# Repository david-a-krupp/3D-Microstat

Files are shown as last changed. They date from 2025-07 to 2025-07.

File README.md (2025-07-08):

# 3D-Microstat
Open-source 3D Clinostat design inspired by iGEM Concordia. This Clinostat was designed by a team of University of Georgia students for the Small Satellite Research Laboratory to support space biology research and microgravity experiments. This final product occupies very little space compared to most other COTS (Commercial-off-the-Shelf) Clinostats, taking up roughly 350 x 300 x 320 mm of space when fully assembled. Build instructions are included below, though the best assembly help will come from viewing the full Microstat assembly (located in CAD files) and viewing the wiring diagram provided.

**Preface -**

This Clinostat build requires a degree of project-specific tailoring. The 140 x 140 mm payload platform is a hard limit for this form factor without increasing the size of the swingarm. The weight restriction varies by geometry and how far from the platform's surface your payload protrudes. The given platform geometry (STL, CAD file) includes M3 fastener holes that can be used for either designing your own mount to add in addition, OR to temporarily secure your payload to the platform. The given Bill of Materials includes all resources used to build the model you see in the CAD model, and pictures/media. I am sure there are cheaper alternatives available from places such as McMaster-Carr that do not leave much excess hardware. Again, this is just what I used to build this at a decent cost. For any recommendations regarding better part selections, please commit an updated file with the updated part description and links so that we can continuously improve this design. Thanks! 

<table>
  <tr>
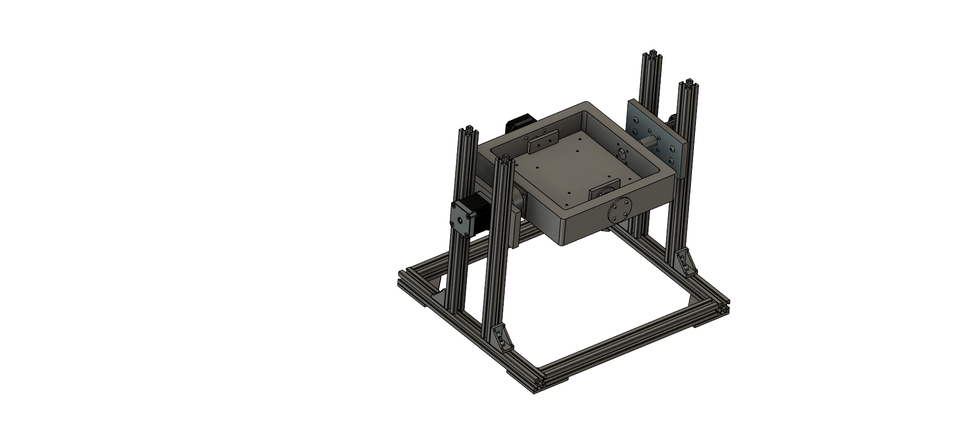
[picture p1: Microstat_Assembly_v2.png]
Microstat CAD Assembly
    <td></td>
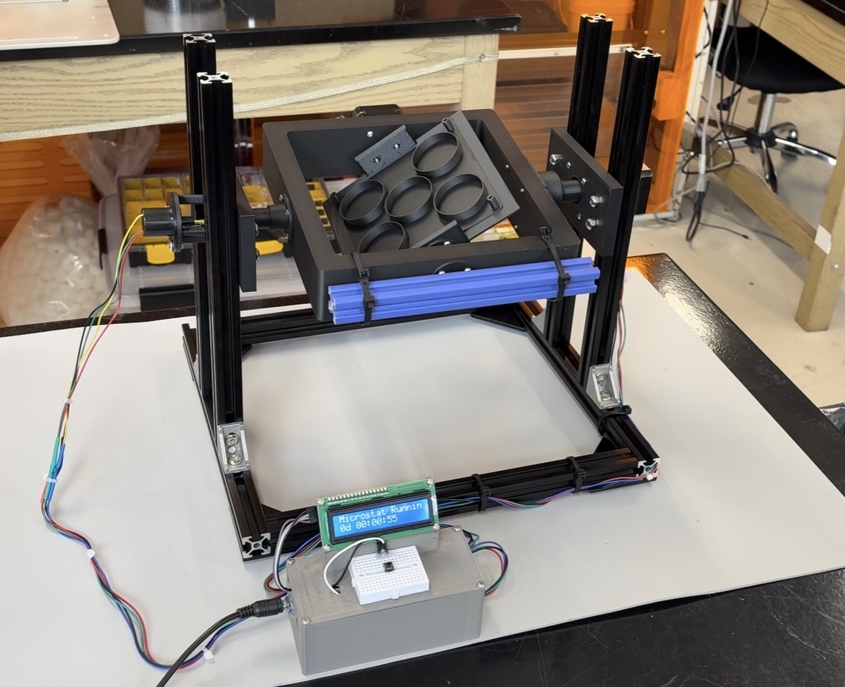
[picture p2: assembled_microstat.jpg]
Assembled Microstat
    <td></td>
  </tr>
</table>

**Build Instructions -** 

Begin by preparing all of the 3D printed parts required for the Microstat. Once the parts are printed, inspect them for any defects or rough edges and carefully remove any excess material or supports. Assemble the main frame by connecting the printed arm, brackets, and base structure as shown in the CAD assembly image. Make sure all moving parts rotate freely and align properly before tightening any fasteners. The 20.5 mm motor should be mounted to the arm before mounting the arm to the frame. Once the 20.5 mm motor is secured, run its 4 wires into the channel in the arm and out the adjacent side. These wires will exit the main assembly through the long rod towards the slip ring mount. 

Next, mount the larger stepper motor to the main axis bracket using the appropriate screws and ensure it is securely fixed in place. Once both motors are mounted, connect the rotating arm to the main axis so that the two axes of rotation are perpendicular, allowing for true 3D rotation. Adjust any extensions or brackets if needed to minimize friction and wobble. Important note: as seen in the provided media, I added balast to the swingarm opposite the side of the 20.5 mm motor to ensure smooth rotation. If you bought the 10pcs aluminum extrusion package from the BoM, I recommend cutting 100 mm off one of the extras and zip tying the 200 mm segment to the swingarm as shown. Otherwise, you may use anything you have that is near the mass of the 20.5 mm motor.

After the mechanical structure is complete, begin wiring the electronics. Connect each stepper motor to its driver module according to the wiring diagram, double-checking the coil pairs to ensure correct rotation. Attach the driver modules to the Arduino Nano, making sure the power and ground connections are secure. Connect the LCD with the I2C backpack to the designated SDA and SCL pins on the Arduino. Install the push button on a separate small breadboard and attach it to the top of the controller case, in front of the LCD. Once the electronics assembly is complete, lower the breadboard with all connections into the case and close it with the lid on top.

Once the wiring is complete, upload the Arduino code provided in this repository to the Nano. Power up the system and test.

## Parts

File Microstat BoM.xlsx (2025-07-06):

Microstat BoM
PRODUCT NAME | Clinostat | INFO |  | #VALUE!
APPROVED BY | David Krupp
DATE OF APPROVAL | 2025-07-01 | White Bold Indicates: Printable Part
ORDER/PART COUNT | 34 | Red Bold Indicates: Part Requiring Order
TOTAL COST | $223.25 | Green Bold Indicates: Ordered Part
PART NUMBER | PART NAME | DESCRIPTION | QUANTITY | UNITS | PART IMAGE | UNIT COST | AMOUNT
1 | Bar Corner Connection (Base) | 4 screwed irregular-pentagon corner connections. TAKES M5 SCREWS (STANDARD/ORDERABLE) [ShortxWxHxThickness] | QUANTITY 1 OF ORDER LINK |  | https://www.amazon.com/Bracket-Anodised-Outside-Aluminum-Extrusion/dp/B07ZQFJ2CK?s=industrial |  | $14.99
2 | Bar 90Deg Connection (Base) | 2 screwed 90Deg connection for upright vertical bars. M5 SCREWS/T-NUTS INCLUDED (STANDARD/ORDERABLE) | QUANTITY 1 OF ORDER LINK |  | https://www.amazon.com/Bracket-Connectors-Aluminum-Extrusion-Accessories/dp/B0B9JVW5X8?s=hi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 |  | $12.99
3 | M3 Fastenings | M3 fasteners for all motor, swivel, blockoff, and non-frame structural componets. | QUANTITY 1 OF ORDER LINK | M3 | https://www.amazon.com/iexcell-Thread-Stainless-Socket-Screws/dp/B07CXKDJ7X?mcid=0fc05dd91ca439b4976eff2272593c81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 |  | $9.96
4 | M5 Fastenings | M5 fasteners needed for frame componets and motor/rod mounting. | QUANTITY 1 OF ORDER LINK | M5 | https://www.amazon.com/Kadrick-Button-Assortment-Stainless-Washers/dp/B0BZ7YZY3D?s=hi |  | $9.99
5 | M5 T-nuts | For assembling the frame. | QUANTITY 1 OF ORDER LINK | M5 | https://www.amazon.com/HELIFOUNER-Pieces-2020-Aluminum-Profile/dp/B0B1LTRYR5?cv_ct_cx=m5%2Bt-nuts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 |  | $5.99
6 | Aluminum Extrusions (300mm) | Diagonally supported long-running base bars (STANDARD/ORDERABLE) [LxWxD] | QUANTITY 2 OF ORDER LINK |  | https://www.amazon.com/Aluminum-Extrusion-European-Standard-7-874inch/dp/B08744RN57?cv_ct_cx=20x20%2BAluminum%2BExtrusion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 |  | $35.98
7 | TMC2209 UART Stepper Motor Drivers | Nema 17 motors require these instead of the DRV8825. The 48mm motor can require up to 2 amps. These supply up to 2.8 amps. | QUANTITY 1 OF ORDER LINK |  | https://www.amazon.com/dp/B08SMDY3SQ?ref=ppx_yo2ov_dt_b_fed_asin_title&th=1 |  | $13.99
8 | 48 mm Nema 17 Stepper Motor | High Torque Motor for main swingarm | QUANTITY 1 OF ORDER LINK |  | https://www.amazon.com/dp/B00PNEQKC0?ref=ppx_yo2ov_dt_b_fed_asin_title |  | $13.99
9 | 20.5 mm Nema 17 Stepper Motor | Small Stepper for inner arm | QUANTITY 1 OF ORDER LINK |  | https://www.amazon.com/dp/B0D22GZFPC?ref=ppx_yo2ov_dt_b_fed_asin_title&th=1 |  | $9.49
10 | Slip Ring | (22 mm, 4-channel, 5 amp maximum) | QUANTITY 1 OF ORDER LINK |  | https://www.aliexpress.us/item/2251832799374262.html |  | $13.49
11 | Arduino Nano Microcontroller | Attached link comes with 3 controllers, only one is needed, no single boards avaliable for cheaper. | QUANTITY 1 OF ORDER LINK |  | https://www.amazon.com/LAFVIN-Board-ATmega328P-Micro-Controller-Arduino/dp/B07G99NNXL?s=industrial |  | $15.99
12 | Breadboards (Mini, 6pcs) | Comes with 6 small breadboards for the controller case. This can be substituted for one larger breadboard for simplicity ***control case edit required***. | QUANTITY 1 OF ORDER LINK |  | https://www.amazon.com/WWZMDiB-SYB-170-Breadboard-Colorful-Multicolored/dp/B0B827VM95?s=industrial |  | $5.99
13 | 1602 LCD Screen (3pcs) | With I2C backpack for wiring simplicity. Comes with 3 pieces. | QUANTITY 1 OF ORDER LINK |  | https://www.amazon.com/Hosyond-Display-Module-Arduino-Raspberry/dp/B0BWTFN9WF?s=industrial |  | $12.99
14 | Jumper Wires | For assembling the Clinostat controller. | QUANTITY 1 OF ORDER LINK |  | https://www.amazon.com/EDGELEC-Breadboard-Optional-Assorted-Multicolored/dp/B07GD2BWPY?s=industrial&sp_csd=d2lkZ2V0TmFtZT1zcF9hdGY |  | $6.98
15 | Terminal Block Connectors | For controller, connects both power supply and the steppers to the breadboards. | QUANTITY 1 OF ORDER LINK |  | https://www.amazon.com/dp/B07H5G7GC6?ref=ppx_yo2ov_dt_b_fed_asin_title |  | $8.99
16 | Female DC Barrel Plug Connector | 16 AWG power supply cable, needs to be attached to a male cable 12V 5amp power supply. | QUANTITY 1 OF ORDER LINK |  | https://www.amazon.com/Pigtails-Connector-Adapter-Security-Surveillance/dp/B0C5DWVGJ8 |  | $9.99
17 | 12V 5A Power Supply | DC Output Jack | QUANTITY 1 OF ORDER LINK |  | https://www.amazon.com/dp/B0CW2PJQLJ?ref=ppx_yo2ov_dt_b_fed_asin_title |  | $9.98
18 | Heat Shrink | For splicing the 20.5 mm Stepper Motor wires with the slip ring interface. Will need to be done on both sides of the slip ring for proper cable length. | QUANTITY 1 OF ORDER LINK |  | https://www.amazon.com/108PCS-Heat-Shrink-Tubing-Kit/dp/B0DRKLWLY5 |  | $4.99
19 | Pushbutton | Push button for Arduino/breadboard. 20 buttons included, only one needed. | QUANTITY 1 OF ORDER LINK |  | https://www.amazon.com/DIYables-Button-Arduino-ESP8266-Raspberry/dp/B0BXKN4TY6?s=electronics |  | $6.49
20 | Outer Arm | PLA, ASA, or ABS. 20% Infill, 0.2 mm or lower layer height recommended. No Supports. | QUANTITY 1 | 200 x 200 x 45 mm
21 | Payload Platform | PLA, ASA, or ABS. 20% Infill, 0.2 mm or lower layer height recommended. Supports needed. | QUANTITY 1 | 140 x 140 x 40 mm
22 | Small Motor Shaft Extension | PLA, ASA, or ABS. 20% Infill, 0.2 mm or lower layer height recommended. | QUANTITY 1 | 35 x 35 x 20 mm
23 | Large Motor Shaft Extension | PLA, ASA, or ABS. 20% Infill, 0.2 mm or lower layer height recommended. | QUANTITY 1 | 45 x 45 x 50 mm
24 | 20 mm Rod Swivel | PLA, ASA, or ABS. 20% Infill, 0.2 mm or lower layer height recommended. | QUANTITY 2 | ⌀40 mm, 15 mm
25 | Slip Ring Mount | PLA, ASA, or ABS. 20% Infill, 0.2 mm or lower layer height recommended. Supports needed. | QUANTITY 1 | ⌀44 mm, 35 mm
26 | Short Rod Blockoff | PLA, ASA, or ABS. 20% Infill, 0.2 mm or lower layer height recommended. | QUANTITY 1 | ⌀40 mm, 2 mm
27 | Short Rod | PLA, ASA, or ABS. 20% Infill, 0.2 mm or lower layer height recommended. | QUANTITY 1 | ⌀15.5 mm, 27 mm
28 | Long Rod | PLA, ASA, or ABS. 20% Infill, 0.2 mm or lower layer height recommended. | QUANTITY 1 | ⌀15.5 mm, 52 mm
29 | Motor Spacer Box | PLA, ASA, or ABS. 20% Infill, 0.2 mm or lower layer height recommended. | QUANTITY 1 | 120 x 60 x 10 mm
30 | Rod Spacer Box | PLA, ASA, or ABS. 20% Infill, 0.2 mm or lower layer height recommended. | QUANTITY 1 | 120 x 60 x 10 mm
31 | Controller Case | PLA, ASA, or ABS. 20% Infill, 0.2 mm or lower layer height recommended. Supports recommended. | QUANTITY 1 | 125 x 60 x 50 mm
32 | Controller Case Lid | PLA, ASA, or ABS. 20% Infill, 0.2 mm or lower layer height recommended. | QUANTITY 1 | 125 x 60 x 52 mm
 |  | TOTAL PARTS | 34 |  |  | TOTAL | $223.25
End

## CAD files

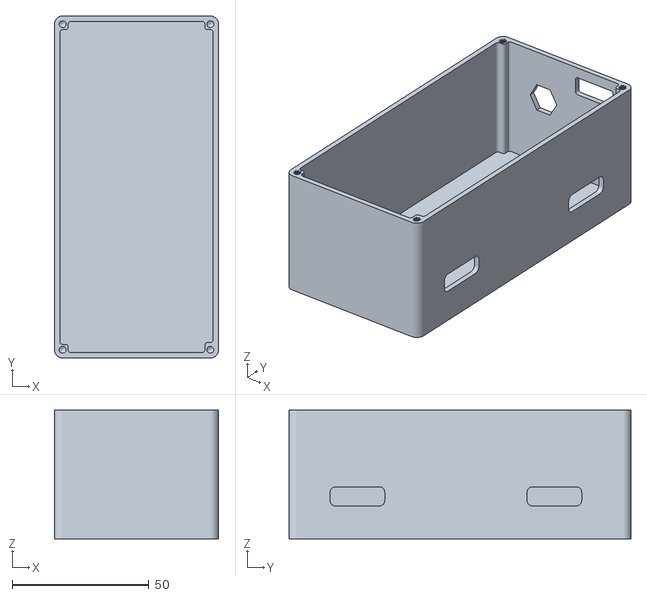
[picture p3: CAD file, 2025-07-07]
Microstat Printable Parts/controller_case_v2.stl
60.0 x 125.0 x 47.0

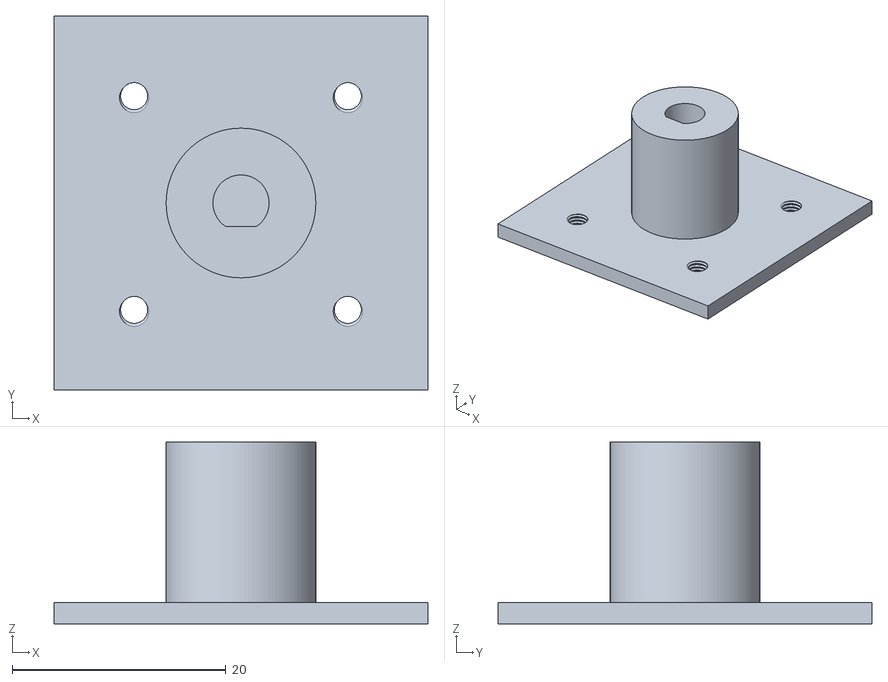
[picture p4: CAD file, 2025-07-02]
Microstat Printable Parts/20mm_shaft_extension.stl
35.0 x 35.0 x 17.0

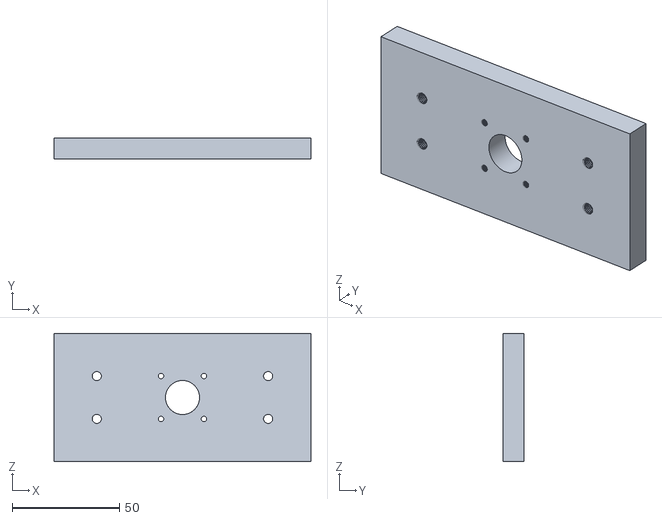
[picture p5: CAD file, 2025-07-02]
Microstat Printable Parts/rod_spacer_box.stl
120.0 x 10.0 x 60.0

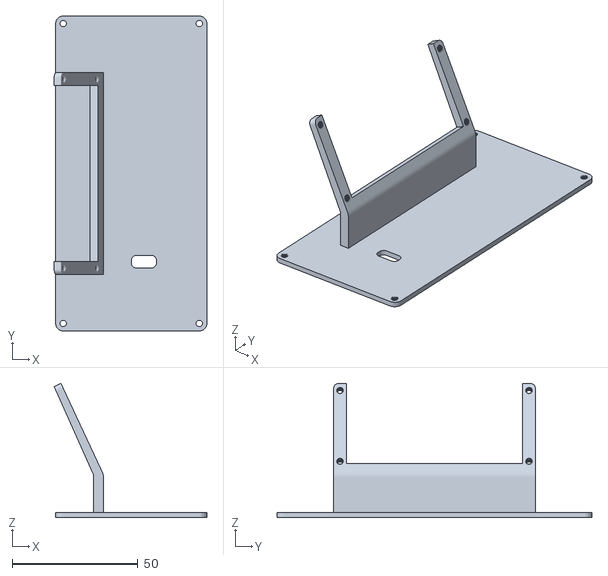
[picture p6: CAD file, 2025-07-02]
Microstat Printable Parts/controller_lid.stl
60.6 x 125.0 x 53.3

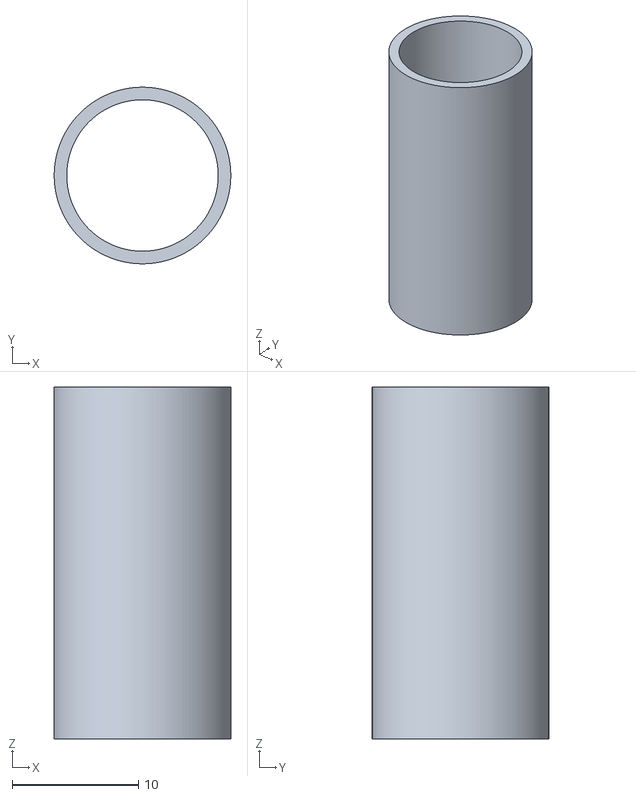
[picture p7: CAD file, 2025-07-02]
Microstat Printable Parts/long_rod.stl
14.0 x 14.0 x 27.9

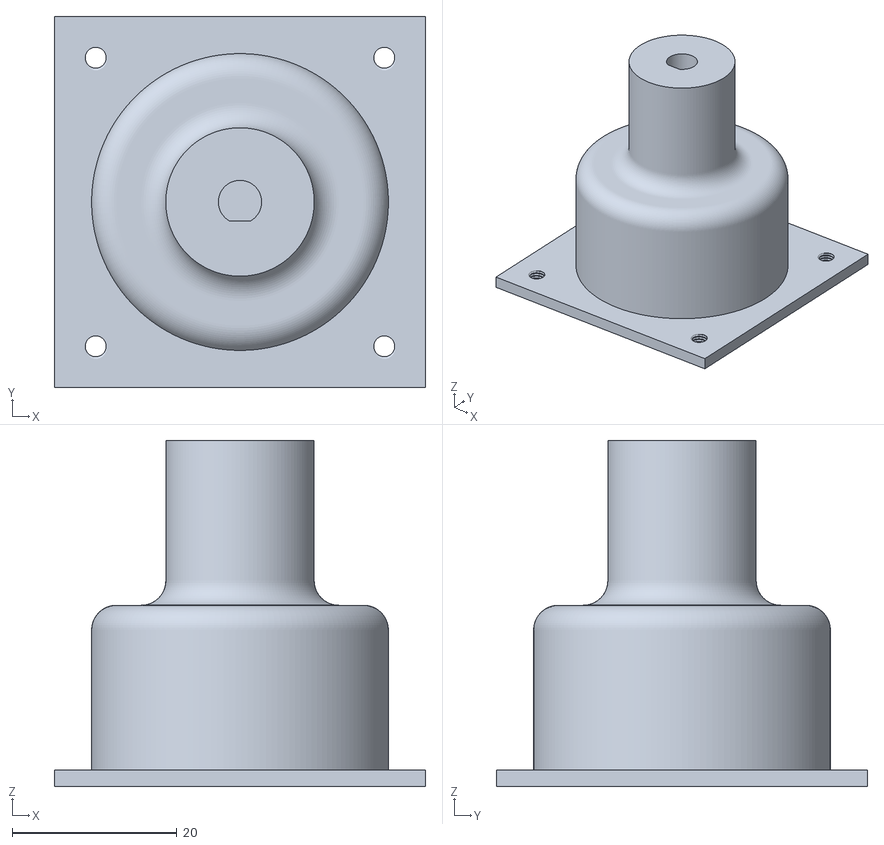
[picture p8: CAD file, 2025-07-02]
Microstat Printable Parts/35mm_shaft_extension.stl
45.0 x 45.0 x 42.0

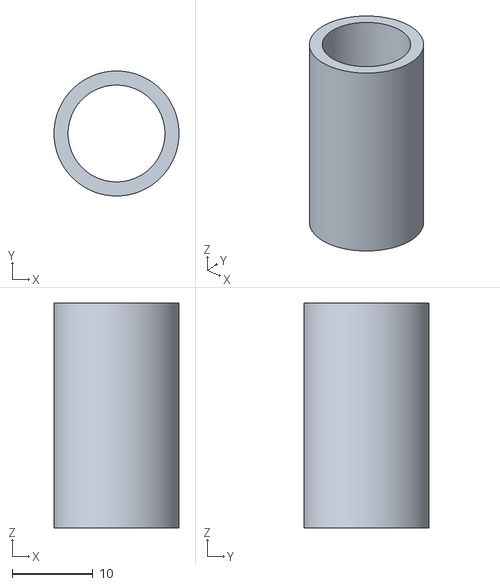
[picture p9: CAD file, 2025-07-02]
Microstat Printable Parts/short_rod.stl
15.5 x 15.5 x 27.9

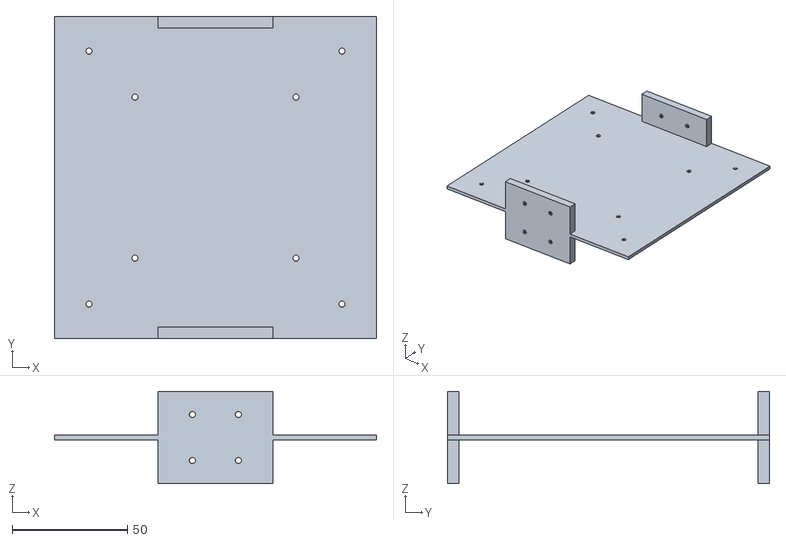
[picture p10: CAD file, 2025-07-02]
Microstat Printable Parts/payload_platform.stl
140.0 x 140.0 x 40.0

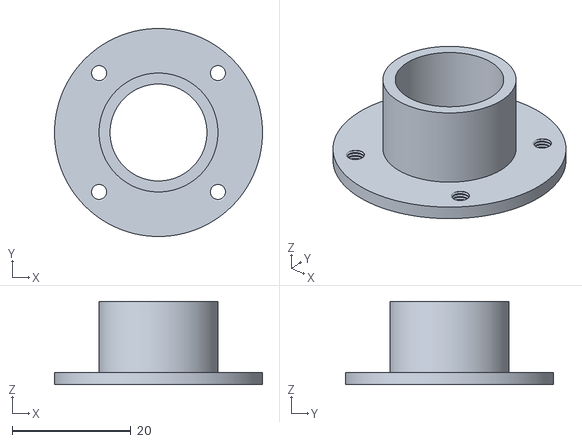
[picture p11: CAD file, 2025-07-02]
Microstat Printable Parts/20mm_swivel.stl
35.0 x 35.0 x 14.0

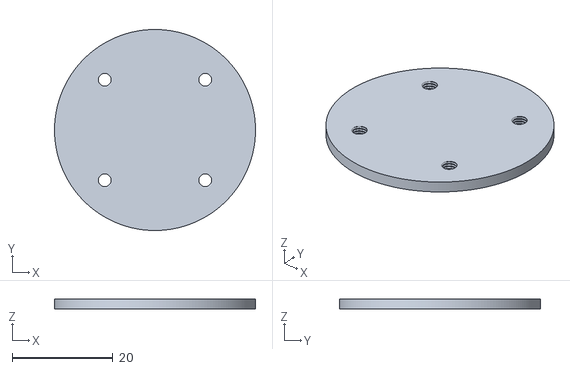
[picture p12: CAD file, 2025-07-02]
Microstat Printable Parts/payload_rod_blockoff.stl
40.0 x 40.0 x 2.00

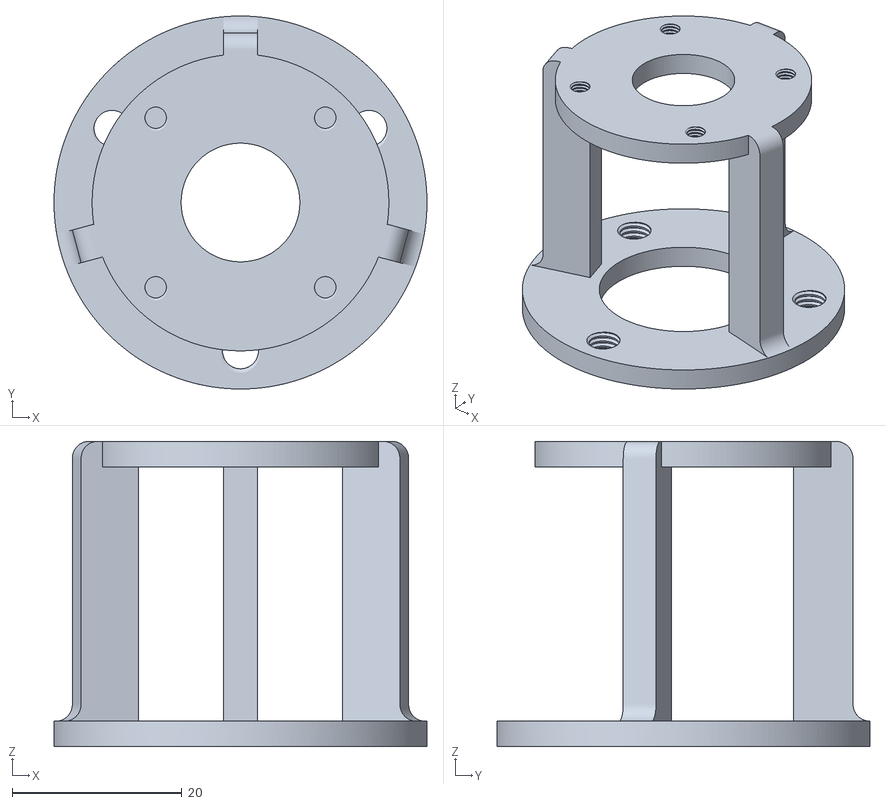
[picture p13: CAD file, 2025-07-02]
Microstat Printable Parts/slip_ring_mount.stl
44.0 x 44.0 x 36.0

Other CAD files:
Microstat Printable Parts/motor_spacer_box.stl
Microstat CAD Files/20.5mm_stepper_motor.f3d
Microstat CAD Files/20mm_shaft_extension.f3d
Microstat CAD Files/20mm_swivel.f3d
Microstat CAD Files/300mm_aluminum_extrusion.f3d
Microstat CAD Files/35mm_shaft_extension.f3d
Microstat CAD Files/48mm_stepper_motor.f3d
Microstat CAD Files/Microstat Assembly v9.f3z
Microstat CAD Files/angle_bracket.f3d
Microstat CAD Files/bracket_plate.f3d
Microstat CAD Files/controller_case_lid.f3d
Microstat CAD Files/controller_case_v2.f3d
Microstat CAD Files/long_rod.f3d
Microstat CAD Files/motor_spacer_box.f3d
Microstat CAD Files/payload_platform.f3d
Microstat CAD Files/rod_blockoff.f3d
Microstat CAD Files/rod_spacer_box.f3d
Microstat CAD Files/short_rod.f3d
Microstat CAD Files/slip_ring_mount.f3d

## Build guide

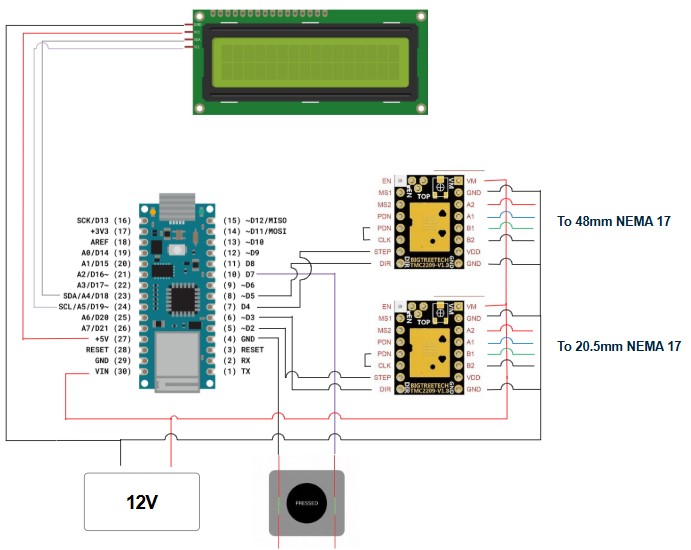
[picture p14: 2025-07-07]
microstat_wiring_diagram.jpg
